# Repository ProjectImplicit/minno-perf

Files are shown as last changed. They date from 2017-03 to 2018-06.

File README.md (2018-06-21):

# minno-perf
Performance test for minno

This repository holds the tests for minno response time player.
Test require an arduino controler. And infrastructure to run minno scripts as well as open-sessame scripts.
You can find the plans to the arduino controlore in the [hardware](hardware) folder.

Experiments each have a folder of its own.

Folder                      | Description
-------                     | -----------
[time](time)                | A sanity test just to see how accurate the browser clock is.
[frame-rate](frame-rate)    | Figure out the measuring errors caused by screen frame rate.
[timeout](timeout)          | Test accuracy of timeouts

### Results

Results for each experiment can be found in the results folder. 
The results are recorded in a separate csv file for each player (each combination of OS & browser is considered a separate player as well os OpenSesame).
OpenSesame files are always prefixed with `open` such as `open-time.csv`.
Minno files are named according to the browser and the following scheme: `{Browser}-{Browser Version}-{OS}-{timestamp}.csv`.

All measurements have common columns describing the hardware and software used to run the test.
Additional columns describe the measurements of each experiment as described in the documuntation.

Following are the common fields:

Column                  | Description
----------------------- | -----------
Browser                 | The browser name (i.e. Firefox)
Browser Version         | Full browser version (i.e. 50.0)
Short Browser Version   | First section of browser version (i.e. 50)
Engine                  | Javascript engine for this browser (i.e. WebKit)
Engine Version          | JS engine version (i.e. 537.36)
OS                      | Operating system (i.e. Mac OS)
OS Version              | Operating system version (i.e. 10.11.6)

Uniquly, open sesame files hold only the measured columns and not the descriptive columns.
The OpenSesame version that was used was OpenSesame version 2.9.7 on Mac OS V10.11.6

### Analysis
Analysis was preformed using [R statistics](www.r-project.org).
The analysis files can be found in the [analysis](analysis) folder.

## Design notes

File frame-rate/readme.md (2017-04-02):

## Display timings

It takes the browser several milliseconds to display visual stimuli.
This delay is caused mainly by the screen refresh rate.
We want to get an idea of how large this delay is, and see if we can reliably measure it from within the browser 
(ideally the player can report the exact times when stimuli are shown/hidden).

### experiment 1

We use the arduino to keypress twice, at a preset interval (`delay`). 
The player displays a stimulus at the first keypress, and hides it at the second keypress.
The arduino measures the time it takes from the initial keypress to the display of the stimulus (`showlatency`).
It also measures the time from the moment the stimulus was displayed to the moment it is hidden (`hidelatency`).
The player measures the time between keypressed (`playerlatency`).

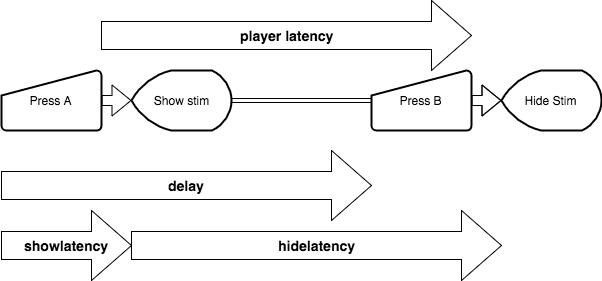
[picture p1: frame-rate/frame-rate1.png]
diagram


The arrows in the diagram represent the various measures as described in the following table:

Name            | Source    | Units | Description
--------------- | --------- | ----- | -----------
showlatency     | arduino   | us    | The latency between the first keypress and the appearance of the stimulus.
hidelatency     | arduino   | us    | The latency between the appearance of the stimulus and its dissapearance.
delay           | arduino   | us    | The delay from the first keypress to the second keypress as set for this trial.
playerlatency   | player    | ms    | The latency between the first and second keypress.

The results can be found in the [results](./results) folder.
The files are each a csv file with the content of the result of a single browser.
The results for OpenSesame can be found in [open-frame-rate.csv](./results/open-frame-rate.csv).

Notably, we needed a version of the arduino script with some additional delay to deal with the slowness of OpenSessame.

#### showlatency
`showlatency` is measured by the arduino from the moment the first key was pressed to the moment the stimulus was displayed.
It is composed of the following:

1. hardware keypress latency
2. os/browser debounce buffer (the computer reads input only so often, see [here](http://stackoverflow.com/questions/8348801/how-large-is-the-average-delay-from-key-presses))
3. player reaction time
4. time until frame

In our case 
(1) is constant (set by the arduino hardware). 
(2) depends on operating system, player type and browser. 
(3) depends on the player type. 
(4) depends on the time that the display was requested.

The imortance of this measure is in gaining some insight to the actual latency between a user action to the player  reaction.
Variability within a browser probably stems from frame-rate problems (as well as timer resolution).
Variability between browsers probably stems from different management of debouncing (2),
though it may be a function of different implementations of js code (3).

#### hidelatency
`hidelatency` is measured by the arduino from the moment the stimulus is displayed to the moment that it is hidden.
It is composed of the (constant) `delay` time, subtract the processing time for the first key (as described previously) and add the processing time for the second key.
The constant parts of the proccessing should cancel out, but variable parts of processing should add to `hidelatency` variability.
Theoretically it should always be a multiple of the frame length (16.6ms).

We test for two delays betwen the keypresses: 100ms and 110ms.
100ms is a multiple of 16.6ms which is the standard length of a frame, and is therefore expected to allow the player to hit the requested timing accurately.
In contrast 110ms is not a multiple of the frame rate, and is expected to give less acurate results.

#### Player Latency
Should be a replication of the time experiment. Measures the time between keypresses as measured by the player.

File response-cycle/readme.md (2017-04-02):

## Response times

We use the arduino to keypress twice, once to setup the experiment, the second a set time (`delay`) after stimulus presentation.
The player displays a stimulus at the first keypress, and hides it at the second keypress.
The arduino measures the time it takes from the initial keypress to the display of the stimulus (`showlatency`).
It also measures the time from the moment the stimulus was displayed to the moment it is hidden (`hidelatency`).
The player measures the time between keypressed (`playerlatency`).

diagram

The arrows in the diagram represent the various measures as described in the following table:

Name            | Source    | Units | Description
--------------- | --------- | ----- | -----------
showlatency     | arduino   | us    | The latency between the first keypress and the appearance of the stimulus.
hidelatency     | arduino   | us    | The latency between the appearance of the stimulus and its dissapearance.
delay           | arduino   | us    | The delay from stimulus display to the second keypress as set for this trial.
playerlatency   | player    | ms    | The latency between the first and second keypress.

The results can be found in the [results](./results) folder.
The files are each a csv file with the content of the result of a single browser.
The results for OpenSesame can be found in [open-response.csv](./results/open-response.csv).

Notably, we needed a version of the arduino script with some additional delay to deal with the slowness of OpenSessame.

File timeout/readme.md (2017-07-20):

### Experiment 3 - Can timers be trusted?
Timers in javascript are notorious for being inaccurate.
The inaccuracy stems from two things: first, browsers update their internal timer only at [specific intervals](https://developer.mozilla.org/en-US/docs/Web/API/WindowOrWorkerGlobalScope/setTimeout#Reasons_for_delays_longer_than_specified),
therefore timeouts can only trigger on these intervals .
This is especially problematic on windows (older windows?) where the polling occurs only every 15ms or so.
The second problem is that javascript is sensitive to background activity,
and external tasks may grab the time where a timeout was supposed to fire.

# experiment 1 (timeout)
This experiment lets a player measure its own timeout latency.
In this experiment the player will trigger a timeout after a predefined period of 50/150/300/800 ms, and measure the logged duration.
In addition to testing minno, the same experiment will be repeated in vanilla JavaScript. 
This is done in order to establish if lag is the result of browser limitations or the player design.

The fields for the csv in this experiment are as follows:

Name            | Source    | Units  | Description
--------------- | --------- | ------ | -----------
Measurement     | player    | String | The name of the measure (minno|vanilla)
delay           | player    | ms     | The length of the timeout as set in the player
latency         | player    | ms     | The measured latency of the delay

The results can be found in the [results folder](./results)
The `Measurement` field does not exist in the [opensesame file](./results/open-timeout.csv).

Notably, tabs out of focus immediately lose the validity of their timers (see for example [here](http://stackoverflow.com/questions/15871942/how-do-browsers-pause-change-javascript-when-tab-or-window-is-not-active).
In particular Safari is sensitive to this and clamps all timeouts after about three minutes without active user interactions (in the tests we use an input to simulate user input).

# experiment 2 (timeout-visual)
This experiment tests the accuracy of a players ability to display a stimulus for a set time.
In the experiment, the player waits for a keypress and then displays the stimulus for a preset time (50/100/110/1000 ms).
The arduino then measures the actual time that the stimulus was displayed.

The player is set to display multiple stimuli, to make sure that the additional stimuli do not cause a delay.

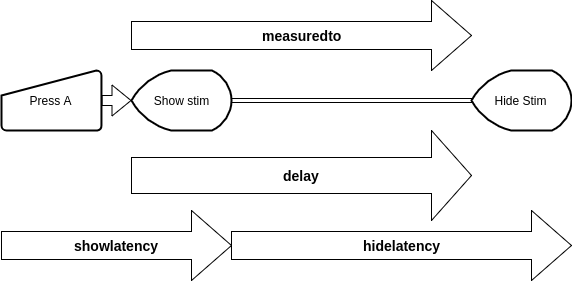
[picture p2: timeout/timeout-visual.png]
diagram


The arrows in the diagram represent the various measures as described in the following table:

Name            | Source    | Units  | Description
--------------- | --------- | ------ | -----------
showlatency     | arduino   | us    | The latency between the keypress and the appearance of the stimulus.
hidelatency     | arduino   | us    | The latency between the appearance of the stimulus and its dissapearance.
delay           | player    | ms    | The delay time set in the player for the display of the stimulus
measuredto      | player    | ms    | The time measured by the player that the stimulus was displayed (at this time simply a measurement of timer accuracy).

The results can be found in the [results_visual folder](./results_visual)

The hideLatency (display duration) can be either higher or lower than required.
It will be higher if the request was made at the end of a frame and ended at the beginning of a frame.
It will be lower if the request was made at the beginning of a frame and ended at the end of a frame.

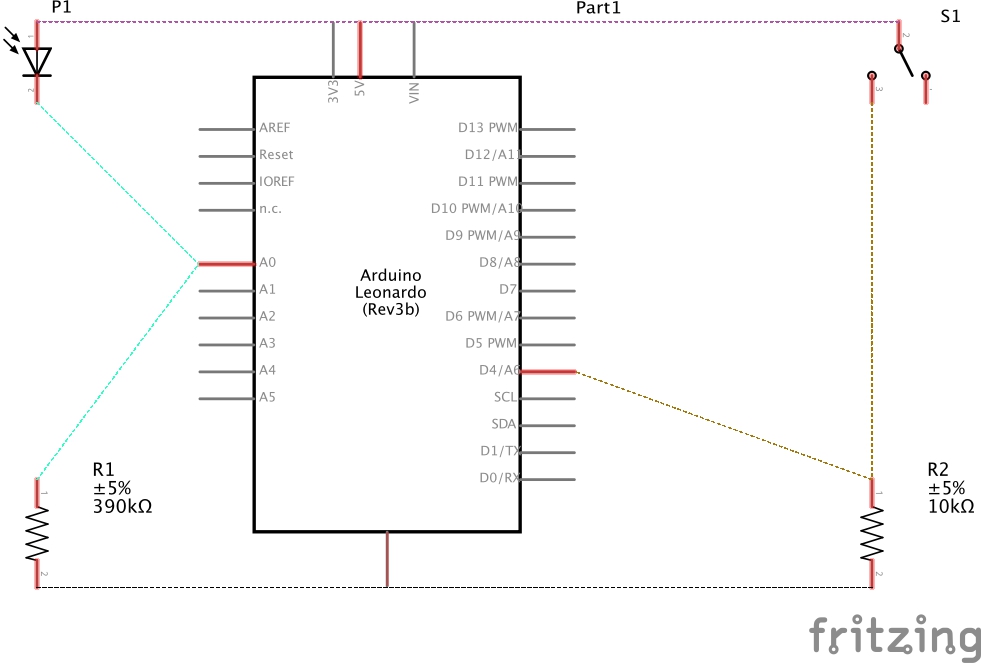
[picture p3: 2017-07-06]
hardware/minno_schem.jpg

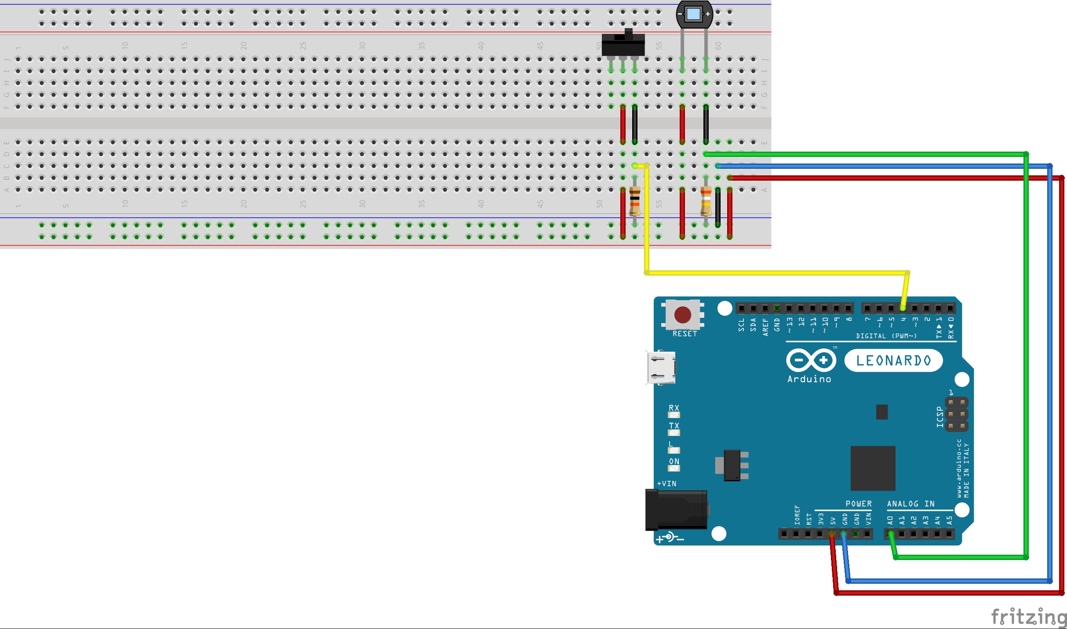
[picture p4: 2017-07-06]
hardware/minno_bb.jpg

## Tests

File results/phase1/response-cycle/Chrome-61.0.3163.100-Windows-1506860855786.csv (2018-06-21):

Browser | Browser Version | Short Browser Version | Engine | Engine Version | OS | OS Version | Measurement | Player Latency | showlatency | hidelatency | delay
Chrome | 61.0.3163.100 | 61 | WebKit | 537.36 | Windows | 10 | minno | 783 | 87132 | 754688 | 300
Chrome | 61.0.3163.100 | 61 | WebKit | 537.36 | Windows | 10 | minno | 343 | 44444 | 359768 | 700
Chrome | 61.0.3163.100 | 61 | WebKit | 537.36 | Windows | 10 | minno | 740 | 41044 | 754672 | 300
Chrome | 61.0.3163.100 | 61 | WebKit | 537.36 | Windows | 10 | minno | 343 | 44448 | 354656 | 700
Chrome | 61.0.3163.100 | 61 | WebKit | 537.36 | Windows | 10 | minno | 744 | 44440 | 759808 | 300
Chrome | 61.0.3163.100 | 61 | WebKit | 537.36 | Windows | 10 | minno | 340 | 41028 | 354640 | 700
Chrome | 61.0.3163.100 | 61 | WebKit | 537.36 | Windows | 10 | minno | 743 | 44440 | 754680 | 300
Chrome | 61.0.3163.100 | 61 | WebKit | 537.36 | Windows | 10 | minno | 344 | 44484 | 354680 | 700
Chrome | 61.0.3163.100 | 61 | WebKit | 537.36 | Windows | 10 | minno | 743 | 44424 | 756376 | 300
Chrome | 61.0.3163.100 | 61 | WebKit | 537.36 | Windows | 10 | minno | 342 | 42760 | 356352 | 700
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

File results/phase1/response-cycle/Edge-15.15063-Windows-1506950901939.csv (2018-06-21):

Browser | Browser Version | Short Browser Version | Engine | Engine Version | OS | OS Version | Measurement | Player Latency | showlatency | hidelatency | delay
Edge | 15.15063 | 15 | EdgeHTML | 15.15063 | Windows | 10 | minno | 366 | 106024 | 383664 | 300
Edge | 15.15063 | 15 | EdgeHTML | 15.15063 | Windows | 10 | minno | 768 | 105916 | 783700 | 700
Edge | 15.15063 | 15 | EdgeHTML | 15.15063 | Windows | 10 | minno | 378 | 105892 | 383656 | 300
Edge | 15.15063 | 15 | EdgeHTML | 15.15063 | Windows | 10 | minno | 770 | 105900 | 783704 | 700
Edge | 15.15063 | 15 | EdgeHTML | 15.15063 | Windows | 10 | minno | 378 | 105912 | 383656 | 300
Edge | 15.15063 | 15 | EdgeHTML | 15.15063 | Windows | 10 | minno | 770 | 104180 | 785416 | 700
Edge | 15.15063 | 15 | EdgeHTML | 15.15063 | Windows | 10 | minno | 378 | 104184 | 385368 | 300
Edge | 15.15063 | 15 | EdgeHTML | 15.15063 | Windows | 10 | minno | 770 | 104196 | 785408 | 700
Edge | 15.15063 | 15 | EdgeHTML | 15.15063 | Windows | 10 | minno | 380 | 104192 | 385360 | 300
Edge | 15.15063 | 15 | EdgeHTML | 15.15063 | Windows | 10 | minno | 779 | 87132 | 785400 | 700
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

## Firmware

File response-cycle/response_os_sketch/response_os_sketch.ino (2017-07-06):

#include "Keyboard.h"

const int swichPin = 4;
const int sensorPin = 0;
const int led = 13;

const int KEY_FIRST = 65; // A
const int KEY_SECOND = 66; // B

unsigned long startTime;
unsigned long showTime;
unsigned long hideTime;

const int THRESHOLD = 700;
const int DELAYS_LENGTH = 2;
const unsigned long int DELAYS[] = {100000, 110000}; // 100ms the delay between keypresses
unsigned long int delayPointer = 9999; // high enough that it will automatically loop back down to 0

// machine states
const int CALIBRATE = 0;
const int LISTEN_SHOW = 1;
const int WAIT = 2;
const int LISTEN_HIDE = 3;
unsigned int state = CALIBRATE;

void setup() {
  pinMode(sensorPin, INPUT);
  pinMode(swichPin, INPUT);
  pinMode(led, OUTPUT);
  
  // initialize control over the keyboard:
  Keyboard.begin();
}

void slowPrint(char chr, int wait){
  Keyboard.press(chr);
  delay(wait);
  Keyboard.releaseAll();
  delay(wait);      
}

void slowPrintLn(String str){  
  const int lngth = str.length();
  for (int i=0; i <= lngth; i++){
    slowPrint(str[i], 100);
  }
  slowPrint('\n', 1000);
}

void loop() {  
  if (digitalRead(swichPin) == LOW) {
    state = CALIBRATE;
  } else {
    unsigned long now = micros();
    switch (state) {
      case CALIBRATE:
        Keyboard.write(KEY_FIRST);
        startTime = now;
        state = LISTEN_SHOW;
        break;
      case LISTEN_SHOW:
        if (analogRead(sensorPin) > THRESHOLD) {
          showTime = now;
          state = WAIT;

          // update delay length
          delayPointer++;
          if (delayPointer >= DELAYS_LENGTH) delayPointer = 0; 
        }
        break;
      case WAIT:
        if (now - showTime >= DELAYS[delayPointer]) {
           Keyboard.write(KEY_SECOND);
           state = LISTEN_HIDE;
        }
        break;
      case LISTEN_HIDE:
        if (analogRead(sensorPin) < THRESHOLD) {                
          hideTime = now;
          delay(100); // let the client bring up the input
          // deltaShow, deltaHide, deltaDisplayed
          slowPrintLn(String(showTime - startTime) + ',' + String(hideTime - showTime) + ',' + String(DELAYS[delayPointer]));
          //Keyboard.print('\n'); // println isn't sending CR for some reason
          state = CALIBRATE;
        }
    }
  
  }

  digitalWrite(led, state == CALIBRATE ? LOW : HIGH);
}

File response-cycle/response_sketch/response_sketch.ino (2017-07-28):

#include "Keyboard.h"

const int swichPin = 4;
const int sensorPin = 0;

const int KEY_FIRST = 65; // A
const int KEY_SECOND = 66; // B

unsigned long startTime;
unsigned long showTime;
unsigned long hideTime;

const int THRESHOLD = 700;
const int DELAYS_LENGTH = 2;
const unsigned long int DELAYS[] = {300000, 700000}; // the delay from seeing the stim to response
unsigned int delayPointer = 99; // high enough that it will automatically loop back down to 0

// machine states
const int CALIBRATE = 0;
const int LISTEN_SHOW = 1;
const int WAIT = 2;
const int LISTEN_HIDE = 3;
unsigned int state = CALIBRATE;

void setup() {
  pinMode(sensorPin, INPUT);
  pinMode(swichPin, INPUT);
  pinMode(LED_BUILTIN, OUTPUT);
  
  // initialize control over the keyboard:
  Keyboard.begin();
}

/*
 * Apparently screens change intensity quite a lot when they are lit
 * This is what we've found represents a reliable change in read.
 * It takes about 1.5ms to run, but this is a price we must accept...
 */
int averageRead(){
  const int ROUNDS = 15;
  int sum = 0;
  for (int i = 0; i<ROUNDS;i++) sum += analogRead(sensorPin);
  return (int) sum / ROUNDS;
}

void slowPrint(char chr, int wait){
  Keyboard.press(chr);
  delay(wait);
  Keyboard.releaseAll();
  delay(wait);      
}

void slowPrintLn(String str){  
  const int lngth = str.length();
  for (int i=0; i <= lngth; i++){
    slowPrint(str[i], 5);
  }
  slowPrint('\n', 200);
}

void loop() {  
  if (digitalRead(swichPin) == LOW) {
    state = CALIBRATE;
  } else {
    unsigned long now = micros();
    switch (state) {
      case CALIBRATE:
        Keyboard.write(KEY_FIRST);
        startTime = now;
        state = LISTEN_SHOW;
        break;
      case LISTEN_SHOW:
        if (averageRead() > THRESHOLD) {
          showTime = now;
          state = WAIT;

          // update delay length
          delayPointer++;
          if (delayPointer >= DELAYS_LENGTH) delayPointer = 0; 
        }
        break;
      case WAIT:
        if (now >= showTime + DELAYS[delayPointer]) {
           Keyboard.write(KEY_SECOND);
           state = LISTEN_HIDE;
        }
        break;
      case LISTEN_HIDE:
        if (averageRead() < THRESHOLD) {
          hideTime = now;
          delay(100); // let the client bring up the input
          slowPrintLn(String(showTime - startTime) + ',' + String(hideTime - showTime));
          state = CALIBRATE;
        }
    }  
  }

  digitalWrite(LED_BUILTIN, state == CALIBRATE ? LOW : HIGH);
}

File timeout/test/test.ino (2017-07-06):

#include "Keyboard.h"

const int swichPin = 4;
const int sensorPin = 0;

const int KEY_FIRST = 65; // A

unsigned long startTime;
unsigned long endTime;

const int THRESHOLD = 700;

// machine states
const int CALIBRATE = 0;
const int ON = 1;
const int OFF = 2;
unsigned int state = CALIBRATE;

void setup() {
  pinMode(sensorPin, INPUT);
  pinMode(swichPin, INPUT);
  pinMode(LED_BUILTIN, OUTPUT);
  
  Serial.begin(9600);
}


int averageRead(){
  const int ROUNDS = 15;  
  int sum = 0;
  for (int i = 0; i<ROUNDS;i++) sum += analogRead(sensorPin);
  return (int) sum / ROUNDS;
}

void loop() {  
  if (digitalRead(swichPin) == LOW) {
    state = CALIBRATE;
  } else {
    unsigned long now = micros();
    //int val = analogRead(sensorPin);
    int val = averageRead();
    //Serial.println((val > 15 ? "ON - " : "OFF - ") + String(val));
    Serial.println(val);
  }

  digitalWrite(LED_BUILTIN, state == CALIBRATE ? LOW : HIGH);
}

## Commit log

2016-09-06 chore(simple): simple test stage 1
2016-11-22 feat(js): added utils
    [Chrome-54.0.2840.98-Mac OS-1479845780572-.csv, Firefox-49.0-Mac OS-1479845903884-.csv, open-time.csv]
2016-11-24 chore(time): added mac safari
    [Safari-10.0.1-Mac OS-1479845781000-.csv]
2016-11-24 fix(format): file names do not end with '-' anymore
    [Chrome-54.0.2840.98-Mac OS-1479845780572.csv, Firefox-49.0-Mac OS-1479845903884.csv, Safari-10.0.1-Mac OS-1479845781000.csv]
2016-11-24 docs(time): fix flow issue
2016-11-24 chore(format): update to valid csv
    [Chrome-54.0.2840.98-Mac OS-1479845780572.csv, Chrome-54.0.2840.98-Mac_OS-1479988314066.csv, Firefox-49.0-Mac OS-1479845903884.csv, Firefox-49.0-Mac_OS-14799884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]
2016-11-24 chore(format): added column for measurement
    [Chrome-54.0.2840.98-Mac_OS-1479988314066.csv, Firefox-49.0-Mac_OS-1479988478880.csv, Safari-10.0-Mac_OS-1479988478880.csv]
2016-11-24 feat(timeout): added OS test
    [open-timeout.csv]
2016-11-24 feat(timeout): Minno script
    [Chrome-54.0.2840.98-Mac_OS-1480021214516.csv, Firefox-49.0-Mac_OS-1480021373099.csv]
2016-11-24 fix(utils): download file now works for safari
    [Safari-10.0-Mac_OS-1480021373099.csv]
2016-11-25 chore(format): update time csv
    [Chrome-54.0.2840.98-Mac_OS-1479988314066.csv, Chrome-54.0.2840.98-Mac_OS-1480034347593.csv, Firefox-49.0-Mac_OS-1479988478880.csv, Firefox-50.0-Mac_OS-14800345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]
2016-11-27 feat(timeout): test vanilla and fix opensesame
    [Chrome-54.0.2840.98-Mac_OS-1480021214516.csv, Chrome-54.0.2840.98-Mac_OS-1480239673891.csv, Firefox-49.0-Mac_OS-1480021373099.csv, Firefox-50.0-Mac_OS-14802398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]
2016-11-27 feat(frame-rate): init opensesame script
2016-12-01 feat(frame-rate): update experiment to record arduino input live
2016-12-01 feat(frame-rate): created sketch
2016-12-04 feat(hardware): added controler plans
    [minno-perf.fzz]
2016-12-04 fix(hardware): updated schematic
    [minno-perf.fzz]
2016-12-11 fix(frame-rate): cosmetics
    [minno-perf.fzz]
2016-12-11 fix(frame-rate): some more tweaking. still doesn't work
2017-03-23 feat(frame-rate): working with results
    [Chrome-56.0.2924.87-Mac_OS-1490111805100.csv, Firefox-51.0-Mac_OS-1490111908181.csv, Safari-10.0-Mac_OS-1490111908300.csv, open-frame-rate.csv]
2017-03-23 docs(frame-rate): full description of the process
2017-03-23 docs(frame-rate): remove repeated sentance
2017-03-24 docs(timeout): improved documentation and recording method
    [Chrome-54.0.2840.98-Mac_OS-1480239673891.csv, Firefox-50.0-Mac_OS-1480239854368.csv, Safari-10.0-Mac_OS-1480239854368.csv, open-timeout.csv]
2017-03-26 feat(timeout): added timeout-visual
    [Chrome-54.0.2840.98-Mac_OS-1480239673891.csv, Chrome-56.0.2924.87-Mac_OS-1490516419546.csv, Firefox-50.0-Mac_OS-1480239854368.csv, Firefox-51.0-Mac_OS-14905166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]
2017-03-26 chore(timeout): fixed folder name
    [Chrome-56.0.2924.87-Mac_OS-1490516419546.csv, Firefox-51.0-Mac_OS-1490516698987.csv, Safari-10.0.2-Mac_OS-1490516419746.csv, open-timeout-visual.csv]
2017-03-26 chore(timeout): remove unneeded files
    [quickrun.csv, subject-0.csv]
2017-03-26 fix(timeout): fix os.csv formatting
    [open-timeout-visual.csv]
2017-03-29 feat(analysis): crostabs for timeout
    [Chrome-54.0.2840.98-Mac_OS-1480239673891.csv, Chrome-56.0.2924.87-Mac_OS-1490516419546.csv, Firefox-50.0-Mac_OS-1480239854368.csv, Firefox-51.0-Mac_OS-14905166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]
2017-03-30 feat(analysis): added time crosstabs
    [Chrome-54.0.2840.98-Mac_OS-1480034347593.csv, Firefox-50.0-Mac_OS-1480034514910.csv, Safari-50.0-Mac_OS-1480034514910.csv, open-time.csv]
2017-04-02 fix(timeout): updated OpenSesame script to display correctly.
    Previously, moving to a form after the stimulus would cause a
    ~100ms delay instead of imidiately hiding it.
    [open-timeout-visual.csv]
2017-04-02 feat(response-cycle): added test
    [Chrome-56.0.2924.87-Mac_OS-1491120714596.csv, Firefox-51.0-Mac_OS-1491120877530.csv, Safari-10.0-Mac_OS-1491120877730.csv, open-response.csv]
2017-04-23 feat(analysis): added analysis for cross os
    [Chrome-55.0.2883.87-Linux-1491316796746.csv, Chrome-55.0.2883.87-Linux-1491330307792.csv, Firefox-52.0-Ubuntu-1491327409832.csv, Firefox-52.0-Ubuntu-1491330023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]
2017-05-04 chore(timeout): added timeout-visual windows
    [Chrome-57.0.2987.133-Windows-1493889384492.csv, Firefox-53.0-Windows-1493890606350.csv, IE-11.0-Windows-1493890148255.csv]
2017-05-04 fix(timeout_visual): readAverage()
    [Chrome-58.0.3029.81-Linux-1493897300275.csv, Firefox-52.0-Ubuntu-1491330023869.csv, Firefox-53.0-Ubuntu-1493561676782.csv, Firefox-53.0-Ubuntu-1493562897966.csv]
2017-05-07 chore(timeout): added windows tests
    [Chrome-57.0.2987.133-Windows-1494155262201.csv, Firefox-53.0-Windows-1494154324939.csv, IE-11.0-Windows-1494154912387.csv]
2017-05-07 fix(timeout_visual): added delay to keyboard input, got FF to make sense
    [Chrome-57.0.2987.133-Windows-1493889384492.csv, Firefox-53.0-Ubuntu-1493562897966.csv, Firefox-53.0-Ubuntu-1494158678212.csv]
2017-05-07 chore(timeout-visual): move opensesame to ubuntu
    [open-timeout-visual.csv]
2017-05-11 feat(timeout-visual): redid Mac browsers
    [Chrome-56.0.2924.87-Mac_OS-1490516419546.csv, Chrome-58.0.3029.96-Mac_OS-1494482221603.csv, Firefox-51.0-Mac_OS-1490516698987.csv, Firefox-52.0-Mac_OS-14944831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]
2017-05-11 chore(timeout): rerun for Mac
    [Chrome-54.0.2840.98-Mac_OS-1480239673891.csv, Chrome-58.0.3029.96-Mac_OS-1494485836997.csv, Firefox-50.0-Mac_OS-1480239854368.csv, Firefox-52.0-Mac_OS-14944854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]
2017-06-08 chore(timeout): recalc with new version
    [Chrome-57.0.2987.133-Windows-1493889384492.csv, Chrome-58.0.3029.110-Mac_OS-1496925592629.csv, Chrome-58.0.3029.81-Linux-1493897300275.csv, Chrome-58.0.3029.96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]
2017-07-06 feat(hardware): moved to 390K ohm for photoresistor
    [minno-perf.fzz, minno.fzz]
2018-06-21 feat(results): uploaded phase1 data, removed old data
    [Chrome-54.0.2840.98-Mac_OS-1480034347593.csv, Chrome-55.0.2883.87-Linux-1491316796746.csv, Chrome-55.0.2883.87-Linux-1491330307792.csv, Chrome-56.0.2924.87-Mac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]
